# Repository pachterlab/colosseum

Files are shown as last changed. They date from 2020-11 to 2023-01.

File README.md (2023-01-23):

# colosseum: open source fraction collector



<p>A modular, highly customizable, open source fraction collector.</p>

<p align="center">
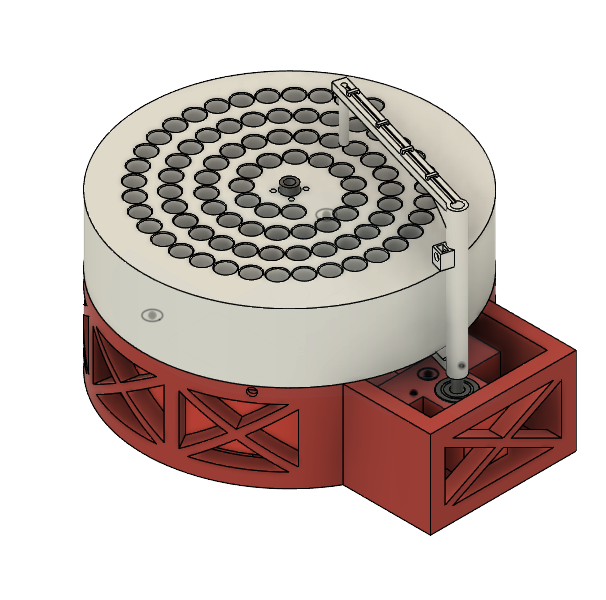
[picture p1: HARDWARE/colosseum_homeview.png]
  
</p>

## Tl;dr
We present colosseum, a low-cost, modular, and automated fluid sampling device for scalable microfluidic applications. The colosseum fraction collector can be built for around $100 using off-the-shelf components, and can be assembled in less than an hour. It uses 3D printed parts and common components that can be easily purchased from many retailers. The device can be run from a Windows, Mac, Linux, or Raspberry Pi computer with an easy-to-use GUI.

<p align="center">
  
</p>

## Table of Contents
1. [What's included?](#whats-included)
2. [Getting Started](#getting-started)
3. [Setting up the hardware](#setting-up-the-hardware)
4. [Installing software](#installing-software)
5. [Startup checklist](#startup-checklist)
6. [Tips/Hints](#tipshints)

## What's included?
* Computer Aided Design (CAD) files of the 3D printed components.
* Controller software (Python) and a graphical user interface (GUI) to control the motor.
* Arduino firmware to send commands to the motors and receive commands from the GUI.
* Bill of materials for sourcing and purchasing materials (up to date as of 1/23/2023).
* Detailed assembly instructions of hardware components.
* Single click executable files for Mac, Windows, Linux, and Raspberry Pi systems.
* A web-based GUI you can run from Chrome without the need to install any Python packages.

## Getting Started
__What do I need to buy?__
The bill of materials with prices and vendor links is available on a [Google Spreadsheet](https://docs.google.com/spreadsheets/d/1GIEj9inR2iLPjJAIjU8kLb73kE2cRr2A/edit?usp=sharing&ouid=103028993012652280196&rtpof=true&sd=true).

__What do I need to make?__
The 3D printed components can be fabricated on any desktop fused filament fabrication (FFF) 3D printer. They were designed using Autodesk Fusion 360, a proprietary CAD software that offers free academic licenses. STL, STEP, IGES, Fusion 360 archive files, and bill of materials are available in the HARDWARE/ folder. They can be used with any slicing software to generate GCode for 3D printing. Here is a [Fusion 360 view](https://a360.co/3r0DND4) of colosseum:

## Setting up the hardware
We have four 3D printed parts for colosseum, which are:
* tube rack
* base
* base plate (support needed)
* dispenser arm (support needed)

The print parameter for these parts are as follows:
* 1.75 mm diameter PLA filament
* nozzle temperature: 215°C
* bed temperature of 60°C
* 10% infill
* 0.2 mm layer height for slicing

### Building colosseum
[This video](https://youtu.be/yG7ECh5GO0o) will guide you through the building process of colosseum.

There is also a [step-by-step guide](https://www.protocols.io/private/C715264790E411EBAAD90A58A9FEAC02) of the assembly.

Here are the steps for building colosseum:
1. 3D print components.
2. Attach set screws to the tube bed.
3. Insert small ball bearings into base.
4. Attach rubber feet on base.
5. Insert rotary shaft into base and fix in place with ball bearing.
6. Screw the stepper motor onto the base (with washers on the hex screws) and attach motor couplings.
7. Screw base plate onto base.
8. Insert ball bearings into the slots on base plate.
9. Insert another rotary shaft into arm and fix with set screw.
10. Insert torsion spring into base plate and arm.
11. Slide the tube bed through the center rotary shaft and align with arm.
12. Tighten all set screws and run!

### Setting up the Arduino
We use the Arduino CNC shield to allow for up to three fraction collectors to be controlled from a computer.

The software is configured to run the stepper motors with 200 steps per revolution at 1/4 microstepping, which translates to 800 steps per rotation. To configure this, it is necessary to add a jumper between the M1 pin of the Arduino CNC shield. More information about microstepping can be found in the product page for the DRV8825 Stepper Motor Driver, which is used by the [CNC shield](http://www.zyltech.com/arduino-cnc-shield-instructions/).

The Arduino should be flashed with the motor_serial_com.ino sketch, available in the firmware/ folder.

Make sure to download and install the [AccelStepper library](https://www.airspayce.com/mikem/arduino/AccelStepper/). To install, unzip the zip file to the libraries sub-folder of your sketchbook.

The fraction collector is driven by an Arduino board that interprets commands sent via USB and sends the signals to control the stepper motor movement. For directions on how to flash an arduino please refer to the official guide: https://www.arduino.cc/en/Guide/HomePage

We recommend that you wrap wires in [cable wraps](https://www.amazon.com/dp/B07FW3GTXB/ref=cm_sw_r_tw_dp_fq83Fb2VRK9QQ?_x_encoding=UTF8&psc=1) and placing your Arduino+CNC shield in a case like [this](https://www.thingiverse.com/thing:3125495).

## Installing software
You can run colosseum on Chrome by going to this link: https://pachterlab.github.io/colosseum/. Running colosseum on the browser platform will not require you to install any software.

To run colosseum locally, you can find the GUI script in the `SOFTWARE/` folder. This GUI is used to interface with a Python script that controls the Arduino via USB.

<p align="center">
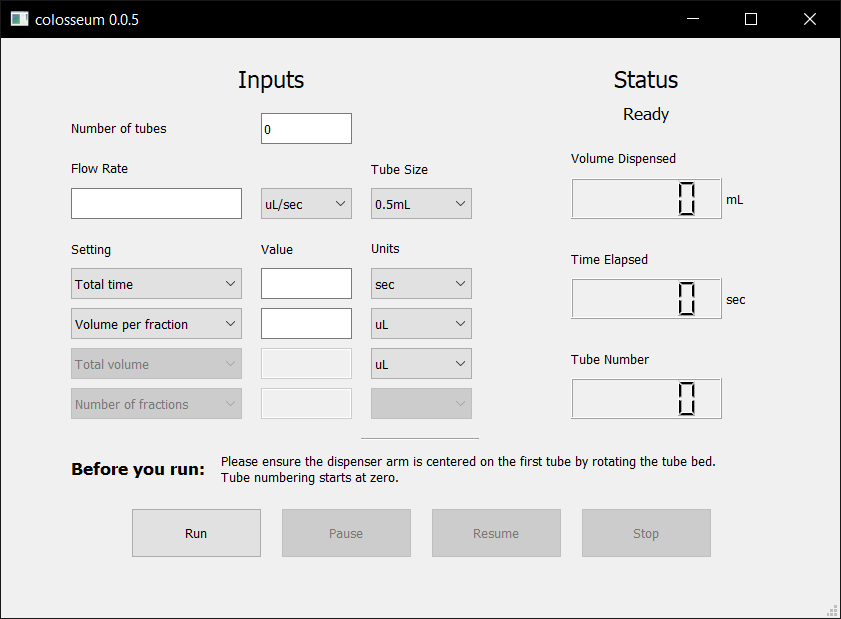
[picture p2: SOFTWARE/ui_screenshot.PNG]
  
</p>

The GUI is provided as a standalone Python package, installable with `pip`. To
install the latest official release, open up the terminal and type:
```
pip install colosseum-ui
```
The Colosseum GUI is now installed and can be started by typing `colosseum` in the termnal. Before you run the system, MAKE SURE YOU HAVE INSTALLED THE ARDUINO FIRMWARE!!

### Manual installation
You may also install the GUI manually by opening up the terminal inside the `SOFTWARE/` folder and typing:
```
pip install .
```

If you get the following error when trying to run `colosseum` on Linux,
```
qt.qpa.plugin: Could not load the Qt platform plugin "xcb" in "" even though it was found.
```
you need to install the appropriate `xcb` library for your Linux distribution.
For Ubuntu users, `xcb` can be installed with the following command:
```
sudo apt install libxcb-xinerama0
```

## Startup Checklist
Before starting the Python controller, make sure
* The Arduino has the firmware uploaded to it
* The Arduino is connected via USB to the computer
* You have appropriately placed jumpers on the CNC Shield to allow for microstepping and hardware enabling (discussed in build video).
* The CNC shield is powered, and that all motors are plugged in to the CNC shield
* The dispenser arm is above the center of the first tube.

## Tips/Hints
Things that we have learned along the way that may help with your build.
* The first tube can be used as a drip tube to catch any drips before you actually start collecting fractions. It will be numbered 0 on the GUI.
* If you hear a scratching noise while you rotate the tube rack, it means that the torsion spring on the arm is scratching the bottom of the tube rack so fold that end of the spring.
* If the dispenser arm does not rotate with the tube rack, it means that the follower on the arm is not correctly touching the grooves of the tube rack.
* Make sure to pull the motor away from the rotary shaft as much as possible so that the pulley belt is taut.

## Safety Considerations
Please review the license before using/developing/distribution colosseum.

The colosseum fraction collector uses 3D printed PLA plastic and standard off the shelf components which do not pose a health hazard if handled correctly. Improper handling of plastics however can create hazards when working with organic solvents.

Before using the colosseum fraction collector in a wetlab environment, please ensure that you have thoroughly tested its functionality for your use case in a dry lab. Once the colosseum fraction collector has been moved into a wetlab, it should not be moved back to a drylab or dry workbench. If you plan to build on the colosseum fraction collector, ensure that you communicate any safety concerns that you may have with your design to potential users and collaborators.

## If you want to contribute to colosseum, feel free to write on the Discussions page on this repo!

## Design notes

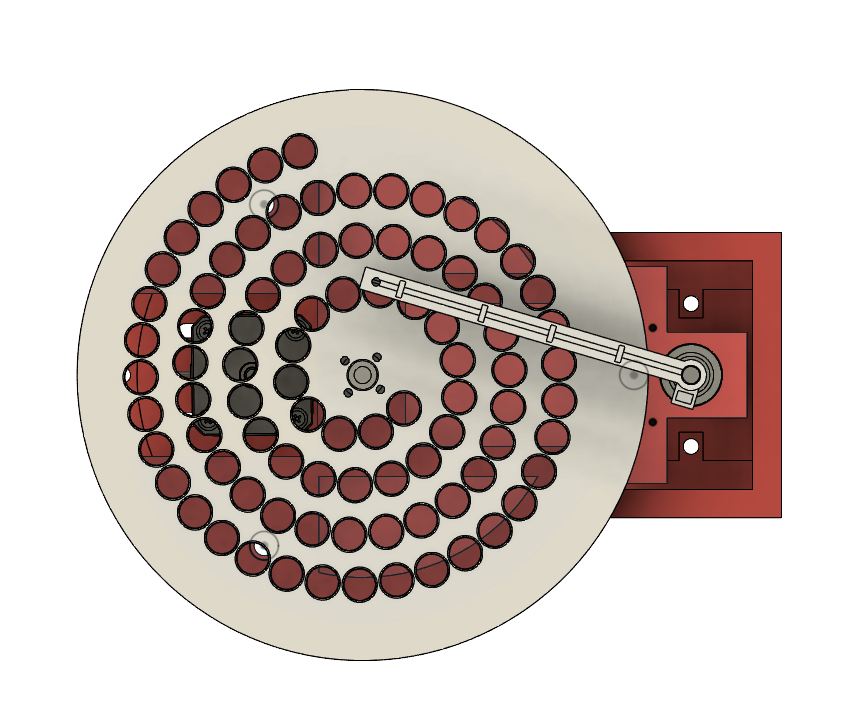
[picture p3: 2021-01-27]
HARDWARE/colosseum_topview.png

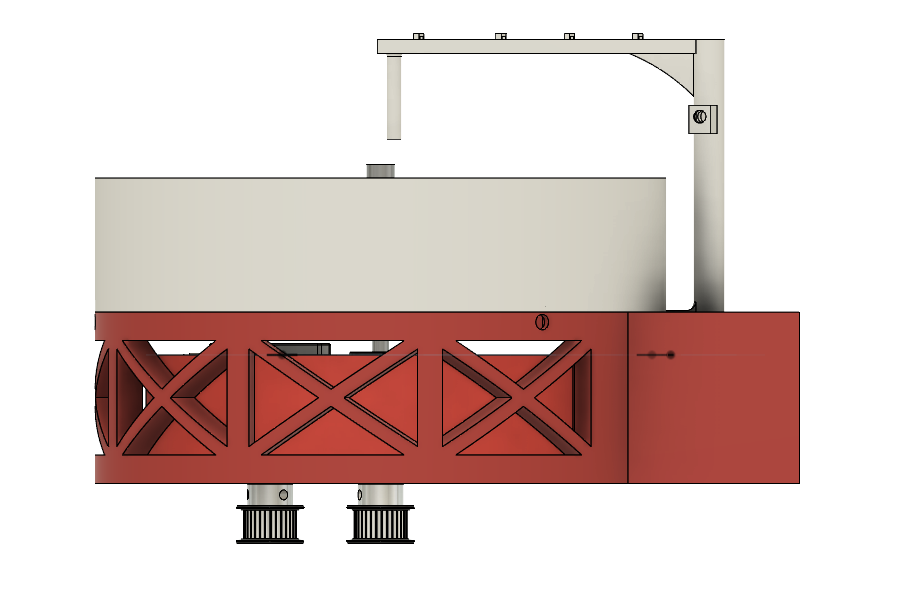
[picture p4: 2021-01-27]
HARDWARE/colosseum_sideview.png

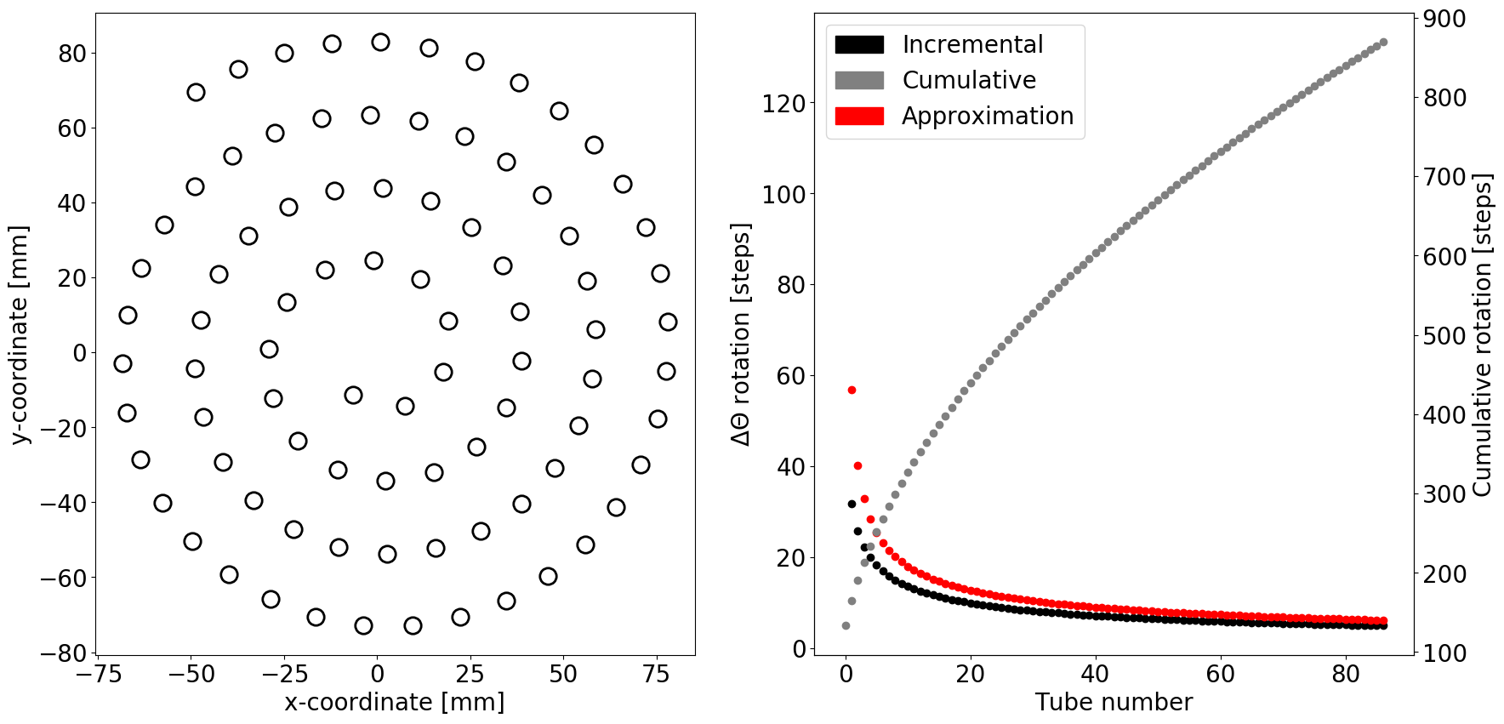
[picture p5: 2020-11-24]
figures/analytical.png

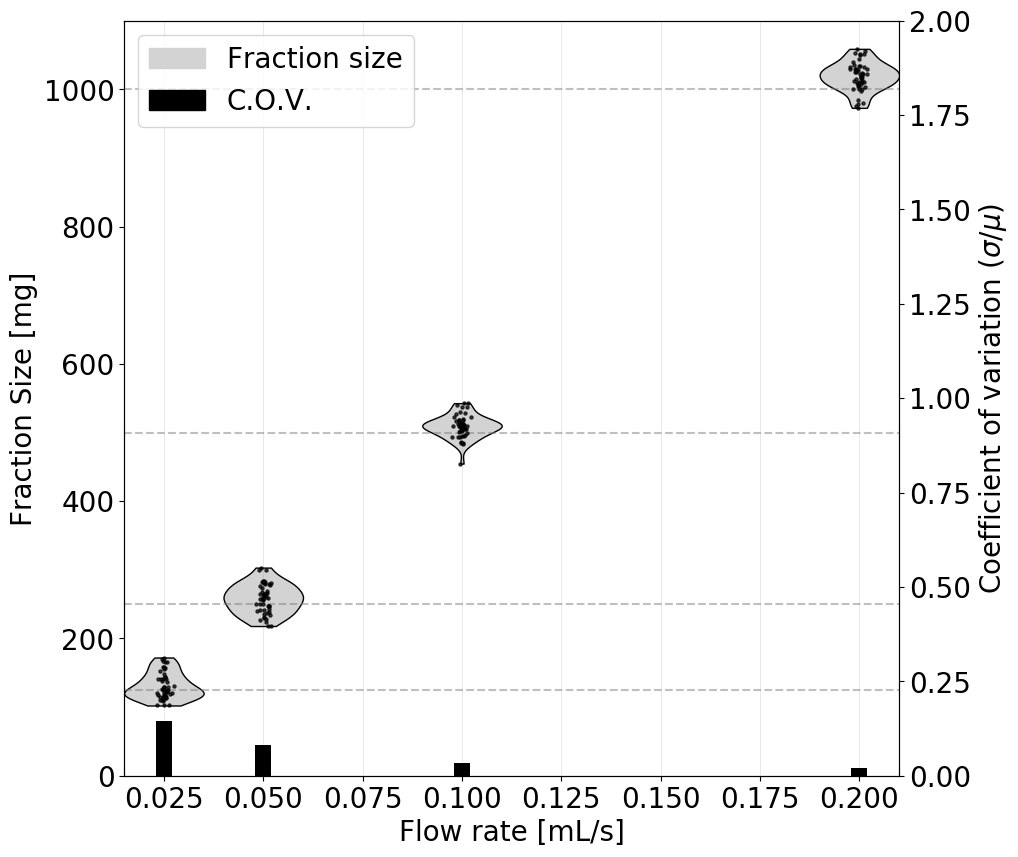
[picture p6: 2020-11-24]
figures/fraction_flowrate.png

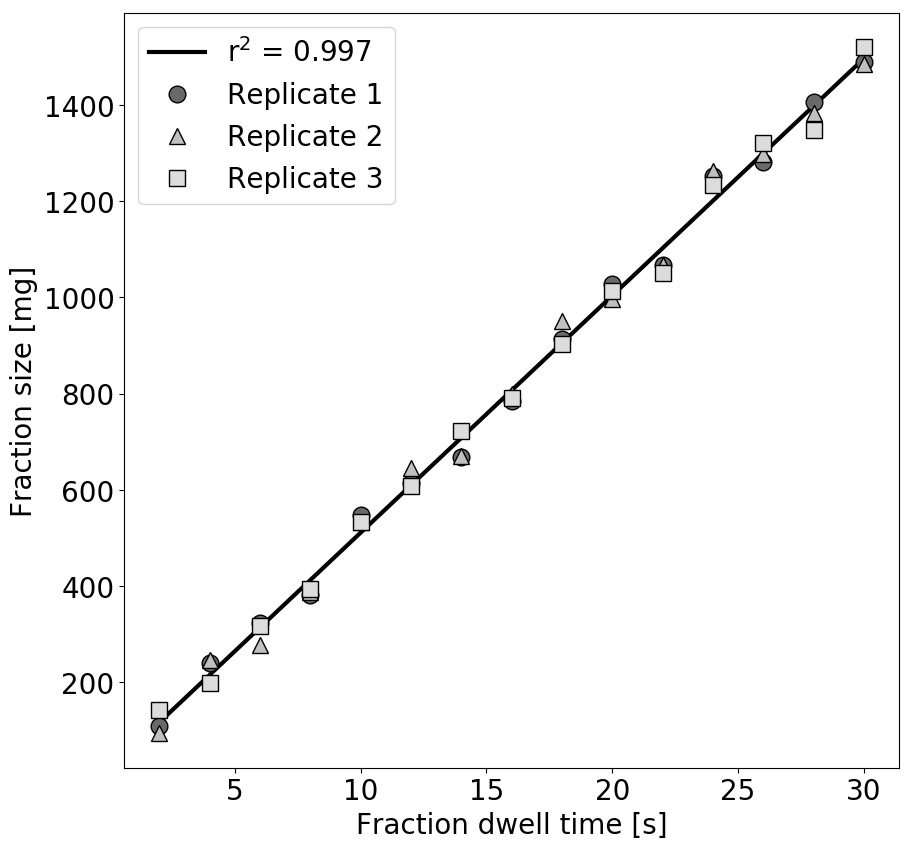
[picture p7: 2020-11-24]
figures/fraction_dwelltime.png

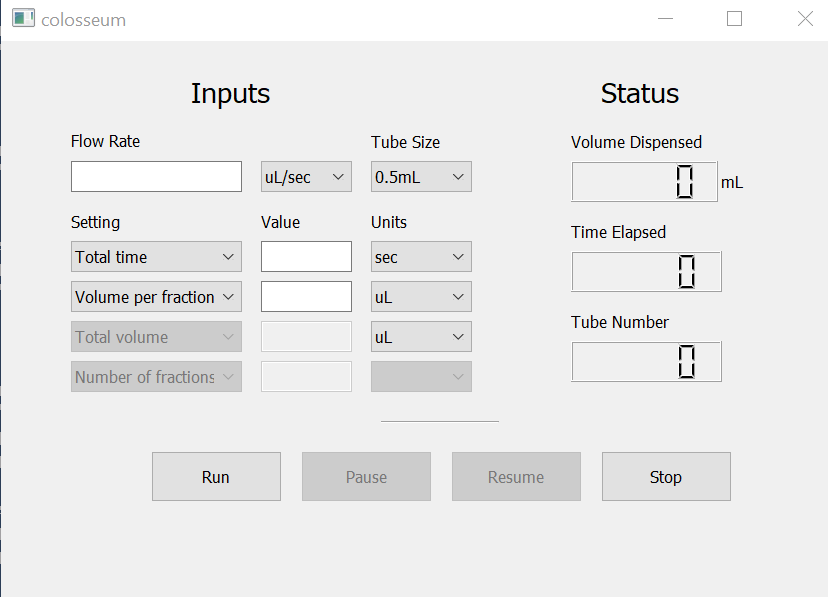
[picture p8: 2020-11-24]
SOFTWARE/colosseum_ui/ui_screenshot.PNG

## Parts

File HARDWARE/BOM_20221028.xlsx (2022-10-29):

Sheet: FracColl
colosseum
Total | $102.29 | *Price may vary based on time of purchase
Part Number | Item Description | Package Cost | Packages for 1 fraction collector | Items per pack | Price per item | Items per fraction collector | Cost for 1 fraction collector | Retailer | Link
1 | 12V power unit (end stripped to fit CNC shield power input) | 15 | 1 | 1 | 15 | 1 | 15 | Amazon | https://www.amazon.com/Kastar-AC-Adapter-Power-LCD/dp/B003TUMDWG?s=electronics
2 | CNC Shield + DRV 8825 Pack | 14.99 | 1 | 1 | 14.99 | 0.25 | 3.7475 | Amazon | https://www.amazon.com/ALMOCN-Printer-Expansion-DRV8825-Stepstick/dp/B09BMVWZGP
3 | Arduino UNO + USB cable | 35.2 | 1 | 1 | 35.2 | 1 | 35.2 | Arduino | https://store-usa.arduino.cc/products/arduino-uno-rev3
4 | Nema 17 Stepper Motor Bipolar 2A 59Ncm 48mm | 13.99 | 1 | 1 | 13.99 | 1 | 13.99 | Amazon | https://www.amazon.com/STEPPERONLINE-Stepper-Bipolar-Connector-compatible/dp/B00PNEQKC0?amp&amp&s=gateway&amp
5 | uxcell HSS Shaft 6mm Dia 150mm Length | 6.96 | 1 | 2 | 3.48 | 2 | 6.96 | Amazon | https://www.amazon.com/uxcell-Lathe-Round-Solid-Length/dp/B07SYHMN6H?s=gateway
6 | uxcell Ball Bearing 6mm x 19mm x 6mm | 6.07 | 1 | 10 | 0.607 | 4 | 2.428 | Amazon | https://www.amazon.com/uxcell-626-2RS-Groove-Bearing-Bearings/dp/B07FMPQP5H?s=gateway
7 | JIUWU 5x10x4mm Miniature Ball Bearing | 7.99 | 1 | 10 | 0.799 | 5 | 3.995 | Amazon | https://www.amazon.com/Miniature-Skateboard-Bearings-MR105ZZ-L-1050ZZ/dp/B00ZHSTKCE?s=gateway
8 | Set Screw Shaft Collar 6mm Bore, 12mm OD, 8mm Width | 21 | 1 | 4 | 5.25 | 2 | 10.5 | Amazon | https://www.amazon.com/Ruland-MSC-6-SS-Collar-Stainless-Metric/dp/B0063KWH7U?s=gateway
9 | WINSINN 2GT Timing Belt Pulley 20 Teeth 5mm Bore 6mm Width | 7.98 | 1 | 5 | 1.596 | 1 | 1.596 | Amazon | https://www.amazon.com/WINSINN-Aluminum-Synchronous-Timing-Printer/dp/B077GNZK3J?s=gateway
10 | WINSINN 2GT Timing Pulley 20 Teeth 6mm Bore 6mm Width | 8.98 | 1 | 5 | 1.796 | 1 | 1.796 | Amazon | https://www.amazon.com/WINSINN-Aluminum-Synchronous-Timing-Printer/dp/B07CXR7SFL?s=gateway
11 | BEMONOC 2GT Rubber Timing Belt 120-2GT-6 60 Teeth | 11.99 | 1 | 10 | 1.199 | 1 | 1.199 | Amazon | https://www.amazon.com/2GT-Timing-Belt-Closed-Loop/dp/B07GQL8ZYH?s=gateway
12 | Hilitchi 110 Pieces Stainless Steel Dowel Pin Assortment Kit | 13.89 | 1 | 110 | 0.1262727273 | 7 | 0.8839090909 | Amazon | https://www.amazon.com/Hilitchi-Stainless-Support-Elements-Assortment/dp/B07F3T5FKL?s=gateway
13 | Round Rubber Feet with Steel Washer Inside | 9.99 | 1 | 10 | 0.999 | 5 | 4.995 | Amazon | https://www.amazon.com/Round-Rubber-Washer-Inside-D19x15xH17mm/dp/B077MB4MGD
 |  | 174.03

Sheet: Sheet1
Fraction Collector
Total | $67.02
Part Number | Item Description | Package Cost | Pkg. for 1 fraction collector | Items per pack | Price per item | Items per fraction collector | Cost for 1 fraction collector | Retailer | Link | Alternative Links (Aliexpress)
1 | 12V power unit (end stripped to fit CNC shield power input) | 15 | 1 | 1 | 15 | 1 | 15 | Amazon | https://amzn.to/2smRmU1
3 | Nema 17 Stepper Motor Bipolar 2A 59Ncm 48mm | 13.99 | 1 | 1 | 13.99 | 1 | 13.99 | Amazon | https://amzn.to/2OsixFJ | https://bit.ly/3poaxEW
4 | uxcell HSS Shaft 6mm Dia 150mm Length | 6.96 | 1 | 2 | 3.48 | 2 | 6.96 | Amazon | https://amzn.to/35GxhXe | https://bit.ly/3rX9U6Z
5 | uxcell Ball Bearing 6mm x 19mm x 6mm | 6.07 | 1 | 10 | 0.607 | 4 | 2.428 | Amazon | https://amzn.to/2q0Z1GZ | https://bit.ly/3b8eYhV
6 | JIUWU 5x10x4mm Miniature Ball Bearing | 7.99 | 1 | 10 | 0.799 | 4 | 3.196 | Amazon | https://amzn.to/2Ovnz49 | https://bit.ly/2ZgT1b8 | (Choose the 5mm x 10mm x 4mm)
7 | Set Screw Shaft Collar 6mm Bore, 12mm OD, 8mm Width | 21 | 1 | 4 | 5.25 | 1 | 5.25 | Amazon | https://amzn.to/2OufigP | https://bit.ly/3u25WM7 | (Choose the 6mm inner diameter model)
8 | WINSINN 2GT Timing Belt Pulley 20 Teeth 5mm Bore 6mm Width | 7.98 | 1 | 5 | 1.596 | 1 | 1.596 | Amazon | https://amzn.to/35K1rsy | https://bit.ly/37euesn | (Choose 5mm bore)
9 | WINSINN 2GT Timing Pulley 20 Teeth 6mm Bore 6mm Width | 8.98 | 1 | 5 | 1.796 | 1 | 1.796 | Amazon | https://amzn.to/2qYr3Dt | https://bit.ly/37euesn | (Choose 6mm bore)
10 | BEMONOC 2GT Rubber Timing Belt 120-2GT-6 60 Teeth | 11.99 | 1 | 10 | 1.199 | 1 | 1.199 | Amazon | https://amzn.to/37IS4Lz | https://bit.ly/3dkWyNJ | (Choose 2GT-120)
11 | Hilitchi 110 Pieces Stainless Steel Dowel Pin Assortment Kit | 13.89 | 1 | 110 | 0.126272727 | 3 | 0.378818182 | Amazon | https://amzn.to/2L285Tl | https://bit.ly/3s0L06f
12 | Round Rubber Feet with Steel Washer Inside | 9.99 | 1 | 10 | 0.999 | 5 | 4.995 | Amazon | https://amzn.to/2XXV1Dq | https://bit.ly/2ZlpYmQ | (Choose 19x15x17)
13 | Torsion Spring 90 Degree Left-Hand Wound, 0.386" OD | 4.63 | 1 | 6 | 0.771666667 | 1 | 0.771666667 | McMaster-Carr | https://www.mcmaster.com/9271k583 | https://bit.ly/3bcJK9B | (Choose 0.8x8x90deg) | Alternative | https://www.amazon.com/dp/B08QN9J157/?coliid=I3IYCJKLM9FWPB&colid=25Z106AEL5JI8 | https://www.amazon.com/dp/B08QNB4M6K/?coliid=I3IYCJKLM9FWPB&colid=25Z106AEL5JI8 | https://www.amazon.com/dp/B08QN8B9CV/?coliid=I3IYCJKLM9FWPB&colid=25Z106AEL5JI8
14 | M3 Hex Screws and Nuts | 10.59 | 1 | 310 | 0.03416129 | 9 | 0.307451613 | Amazon | https://amzn.to/33ABZ7G | https://bit.ly/3poDBfw
15 | M5 Hex Screws and Nuts | 9.99 | 1 | 70 | 0.142714286 | 8 | 1.141714286 | Amazon | https://amzn.to/2OMVYdC
16 | M3 Washers | 8.49 | 1 | 300 | 0.0283 | 4 | 0.1132 | Amazon | https://amzn.to/3rVEjTX | https://bit.ly/3jSpdLi
17 | 6mm Flange Coupling | 11.69 | 1 | 4 | 2.9225 | 1 | 2.9225 | Amazon | https://amzn.to/2YfLFEj | https://bit.ly/3qqrtMr | (Choose 6mm)

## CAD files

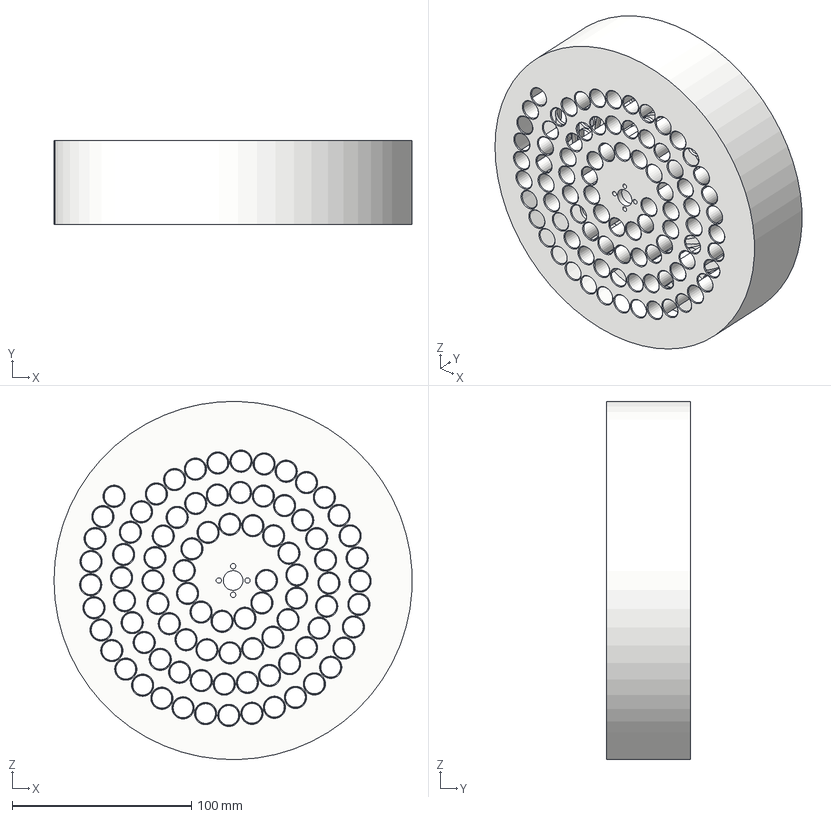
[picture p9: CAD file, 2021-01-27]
HARDWARE/colosseum_tubebed.step
199.9 x 47.0 x 199.9 mm

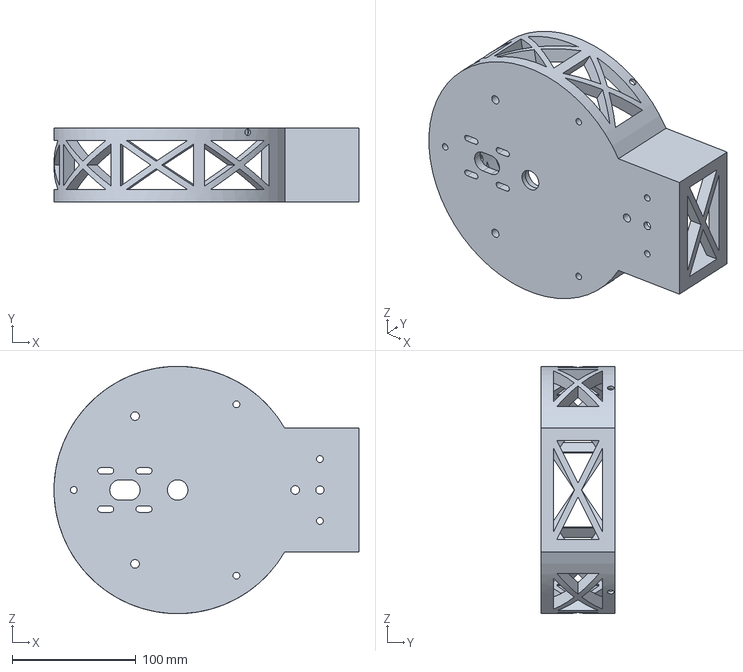
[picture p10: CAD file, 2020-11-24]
HARDWARE/colosseum_base.step
246.6 x 60.0 x 200.0 mm

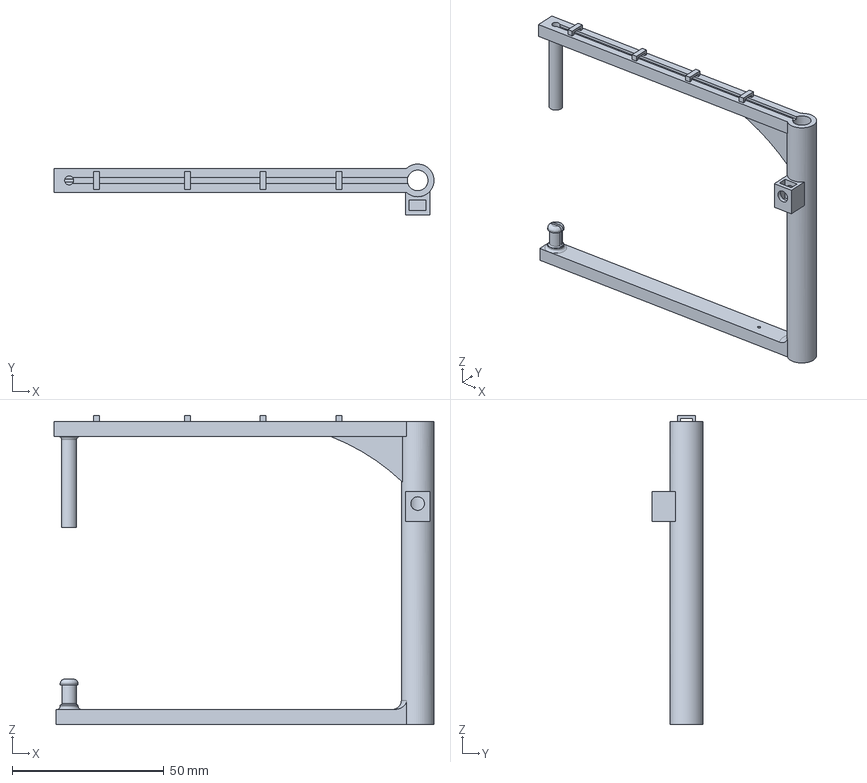
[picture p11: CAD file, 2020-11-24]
HARDWARE/colosseum_arm.step
125.4 x 16.8 x 102.0 mm

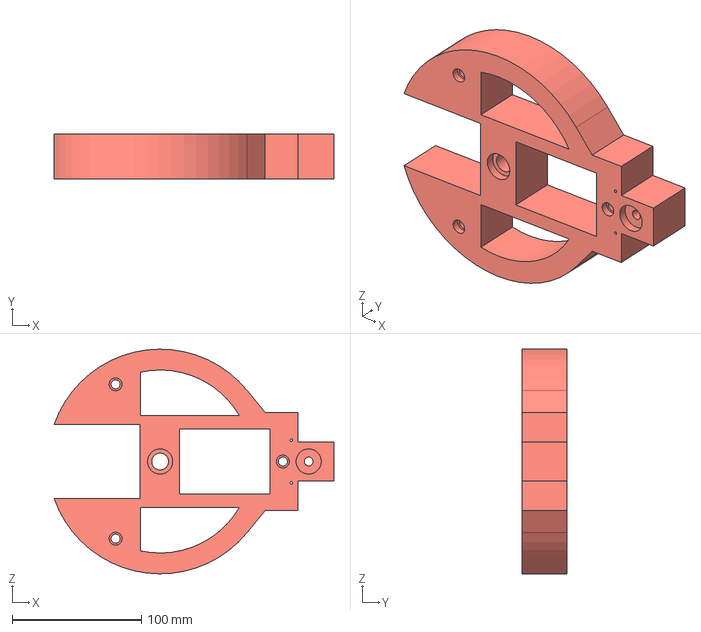
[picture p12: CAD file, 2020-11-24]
HARDWARE/colosseum_baseplate.step
216.8 x 35.0 x 174.0 mm

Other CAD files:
HARDWARE/colosseum_arm.f3d
HARDWARE/colosseum_arm.iges
HARDWARE/colosseum_arm.stl
HARDWARE/colosseum_base.f3d
HARDWARE/colosseum_base.iges
HARDWARE/colosseum_base.stl
HARDWARE/colosseum_baseplate.f3d
HARDWARE/colosseum_baseplate.iges
HARDWARE/colosseum_baseplate.stl
HARDWARE/colosseum_tubebed.f3d
HARDWARE/colosseum_tubebed.iges
HARDWARE/colosseum_tubebed.stl

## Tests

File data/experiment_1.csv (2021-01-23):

Flow rate (uL/s) | Tube Number | Before (g) | After (g) | Difference (g) | Percent error from 1 (%)
6.25 | 1 | 1.066 | 2.063 | 0.997 | -0.3
6.25 | 2 | 1.068 | 2.027 | 0.959 | -4.1
6.25 | 3 | 1.068 | 2.027 | 0.959 | -4.1
6.25 | 4 | 1.068 | 2.079 | 1.011 | 1.1
6.25 | 5 | 1.068 | 2.053 | 0.985 | -1.5
6.25 | 6 | 1.069 | 2.048 | 0.979 | -2.1
6.25 | 7 | 1.045 | 2.04 | 0.995 | -0.5
6.25 | 8 | 1.054 | 2.049 | 0.995 | -0.5
6.25 | 9 | 1.061 | 2.034 | 0.973 | -2.7
6.25 | 10 | 1.063 | 2.078 | 1.015 | 1.5
6.25 | 11 | 1.063 | 2.057 | 0.994 | -0.6
6.25 | 12 | 1.067 | 2.033 | 0.966 | -3.4
6.25 | 13 | 1.062 | 2.067 | 1.005 | 0.5
6.25 | 14 | 1.062 | 2.01 | 0.948 | -5.2
6.25 | 15 | 1.057 | 2.043 | 0.986 | -1.4
6.25 | 16 | 1.06 | 2.026 | 0.966 | -3.4
6.25 | 17 | 1.06 | 2.069 | 1.009 | 0.9
6.25 | 18 | 1.064 | 2.023 | 0.959 | -4.1
6.25 | 19 | 1.065 | 2.061 | 0.996 | -0.4
6.25 | 20 | 1.056 | 2.084 | 1.028 | 2.8
6.25 | 21 | 1.055 | 2.042 | 0.987 | -1.3
6.25 | 22 | 1.072 | 2.029 | 0.957 | -4.3
6.25 | 23 | 1.068 | 2.065 | 0.997 | -0.3
6.25 | 24 | 1.06 | 2.058 | 0.998 | -0.2
6.25 | 25 | 1.064 | 2.064 | 1 | 0
6.25 | 26 | 1.053 | 2.034 | 0.981 | -1.9
6.25 | 27 | 1.054 | 2.063 | 1.009 | 0.9
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

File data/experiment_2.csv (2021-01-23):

Trial | Tube number | Dwell time (s) | Before (g) | After (g) | Difference (g) | Expected (g) | Percent error (%)
1 | 1 | 12 | 1.055 | 1.128 | 0.073 | 0.075 | -2.666666667
1 | 2 | 24 | 1.064 | 1.187 | 0.123 | 0.15 | -18
1 | 3 | 36 | 1.058 | 1.281 | 0.223 | 0.225 | -0.8888888889
1 | 4 | 48 | 1.057 | 1.329 | 0.272 | 0.3 | -9.333333333
1 | 5 | 60 | 1.063 | 1.385 | 0.322 | 0.375 | -14.13333333
1 | 6 | 72 | 1.059 | 1.538 | 0.479 | 0.45 | 6.444444444
1 | 7 | 84 | 1.064 | 1.587 | 0.523 | 0.525 | -0.380952381
1 | 8 | 96 | 1.066 | 1.66 | 0.594 | 0.6 | -1
1 | 9 | 108 | 1.053 | 1.72 | 0.667 | 0.675 | -1.185185185
1 | 10 | 120 | 1.069 | 1.789 | 0.72 | 0.75 | -4
1 | 11 | 132 | 1.066 | 1.895 | 0.829 | 0.825 | 0.4848484848
1 | 12 | 144 | 1.055 | 1.954 | 0.899 | 0.9 | -0.1111111111
1 | 13 | 156 | 1.063 | 2.034 | 0.971 | 0.975 | -0.4102564103
1 | 14 | 168 | 1.063 | 2.042 | 0.979 | 1.05 | -6.761904762
1 | 15 | 180 | 1.063 | 2.257 | 1.194 | 1.125 | 6.133333333
1 | 16 | 192 | 1.054 | 2.239 | 1.185 | 1.2 | -1.25
1 | 17 | 204 | 1.064 | 2.333 | 1.269 | 1.275 | -0.4705882353
1 | 18 | 216 | 1.052 | 2.423 | 1.371 | 1.35 | 1.555555556
1 | 19 | 228 | 1.046 | 2.412 | 1.366 | 1.425 | -4.140350877
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

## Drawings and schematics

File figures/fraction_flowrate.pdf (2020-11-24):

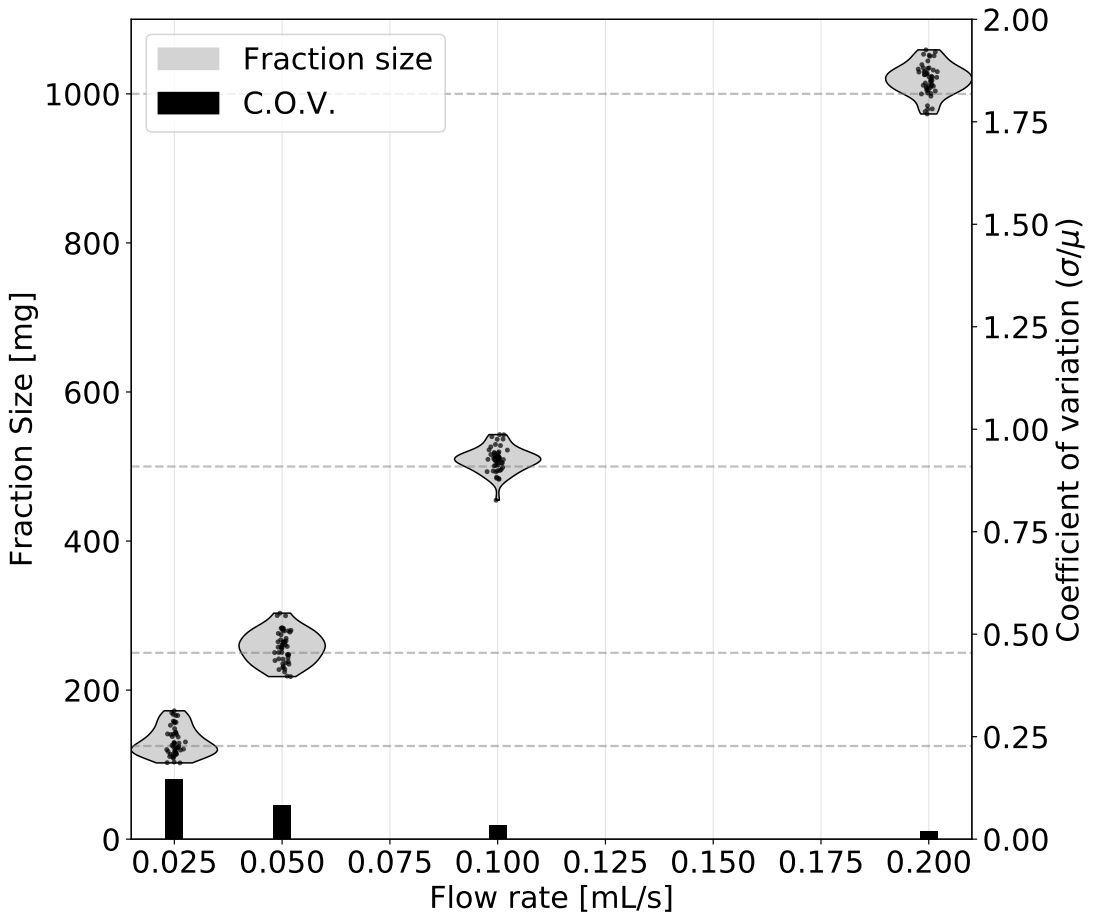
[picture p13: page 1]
ficie; ria; tio; Fraction size C.O.V.

Fraction Size [mg]

Flow rate [mL/s]

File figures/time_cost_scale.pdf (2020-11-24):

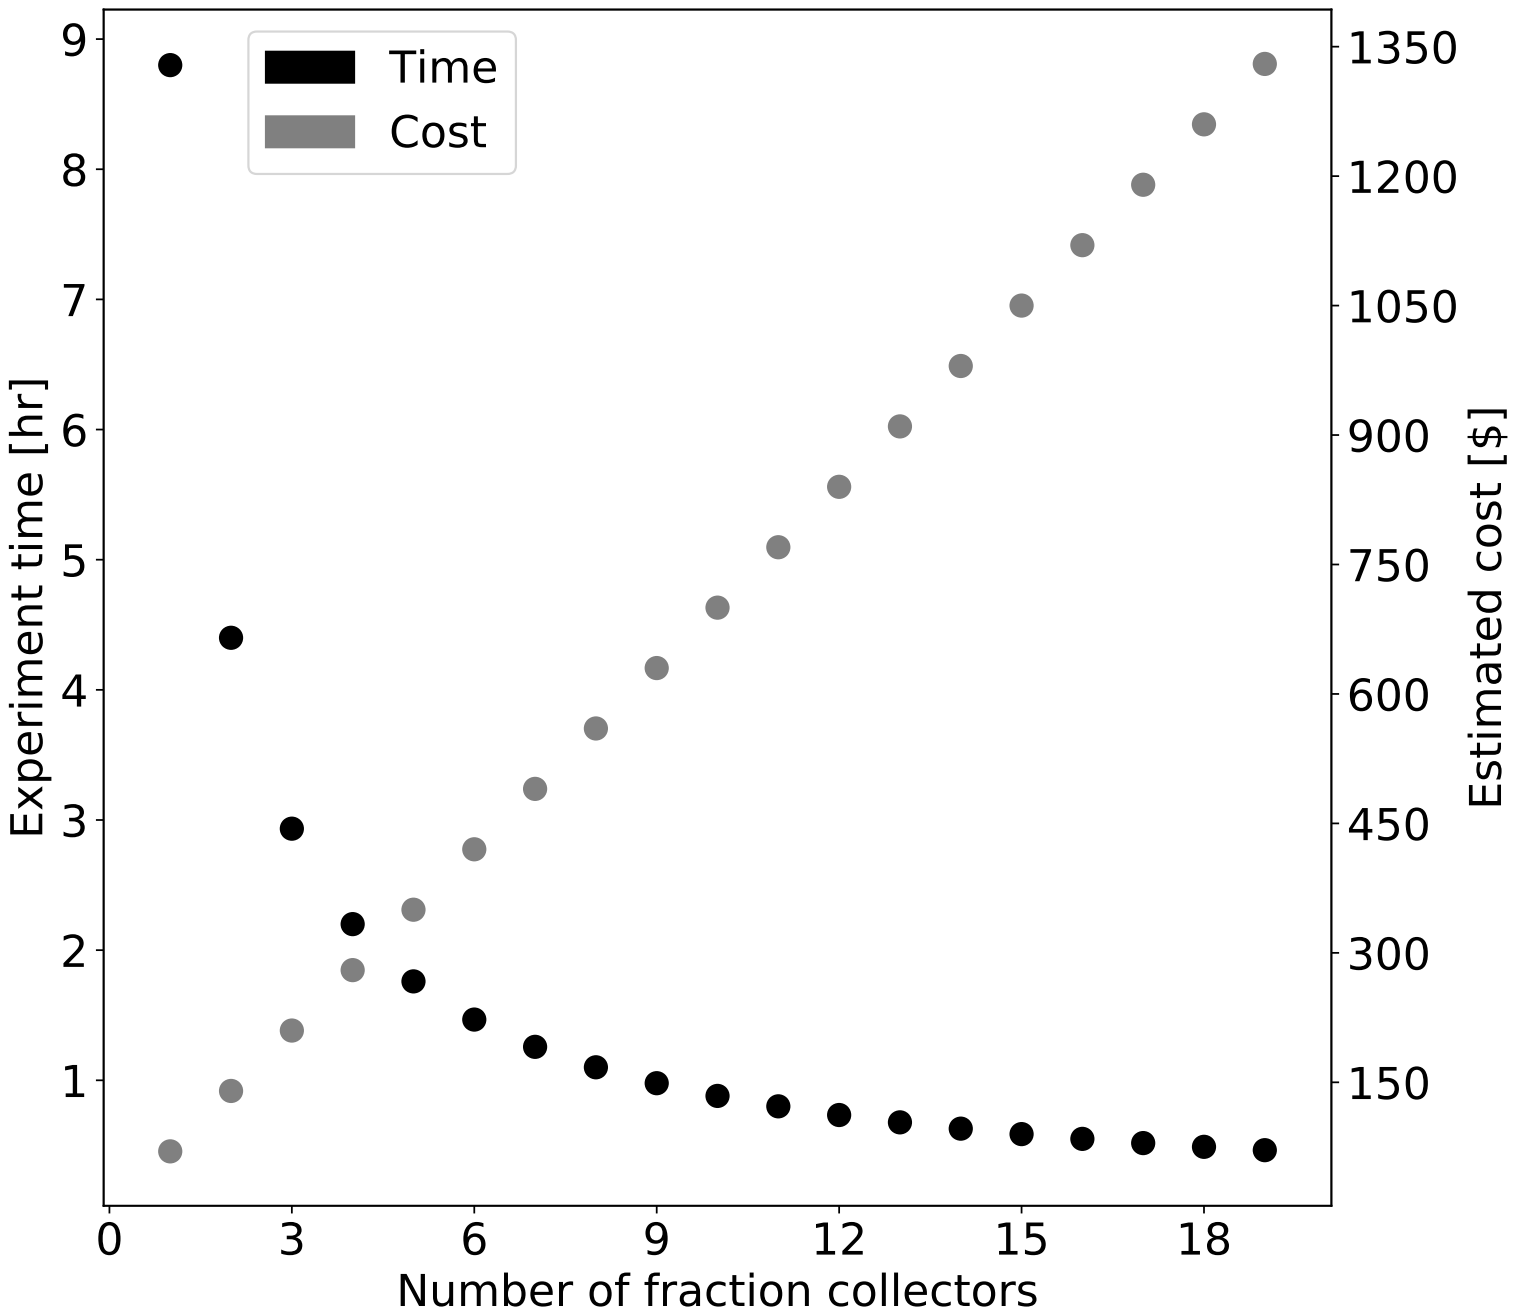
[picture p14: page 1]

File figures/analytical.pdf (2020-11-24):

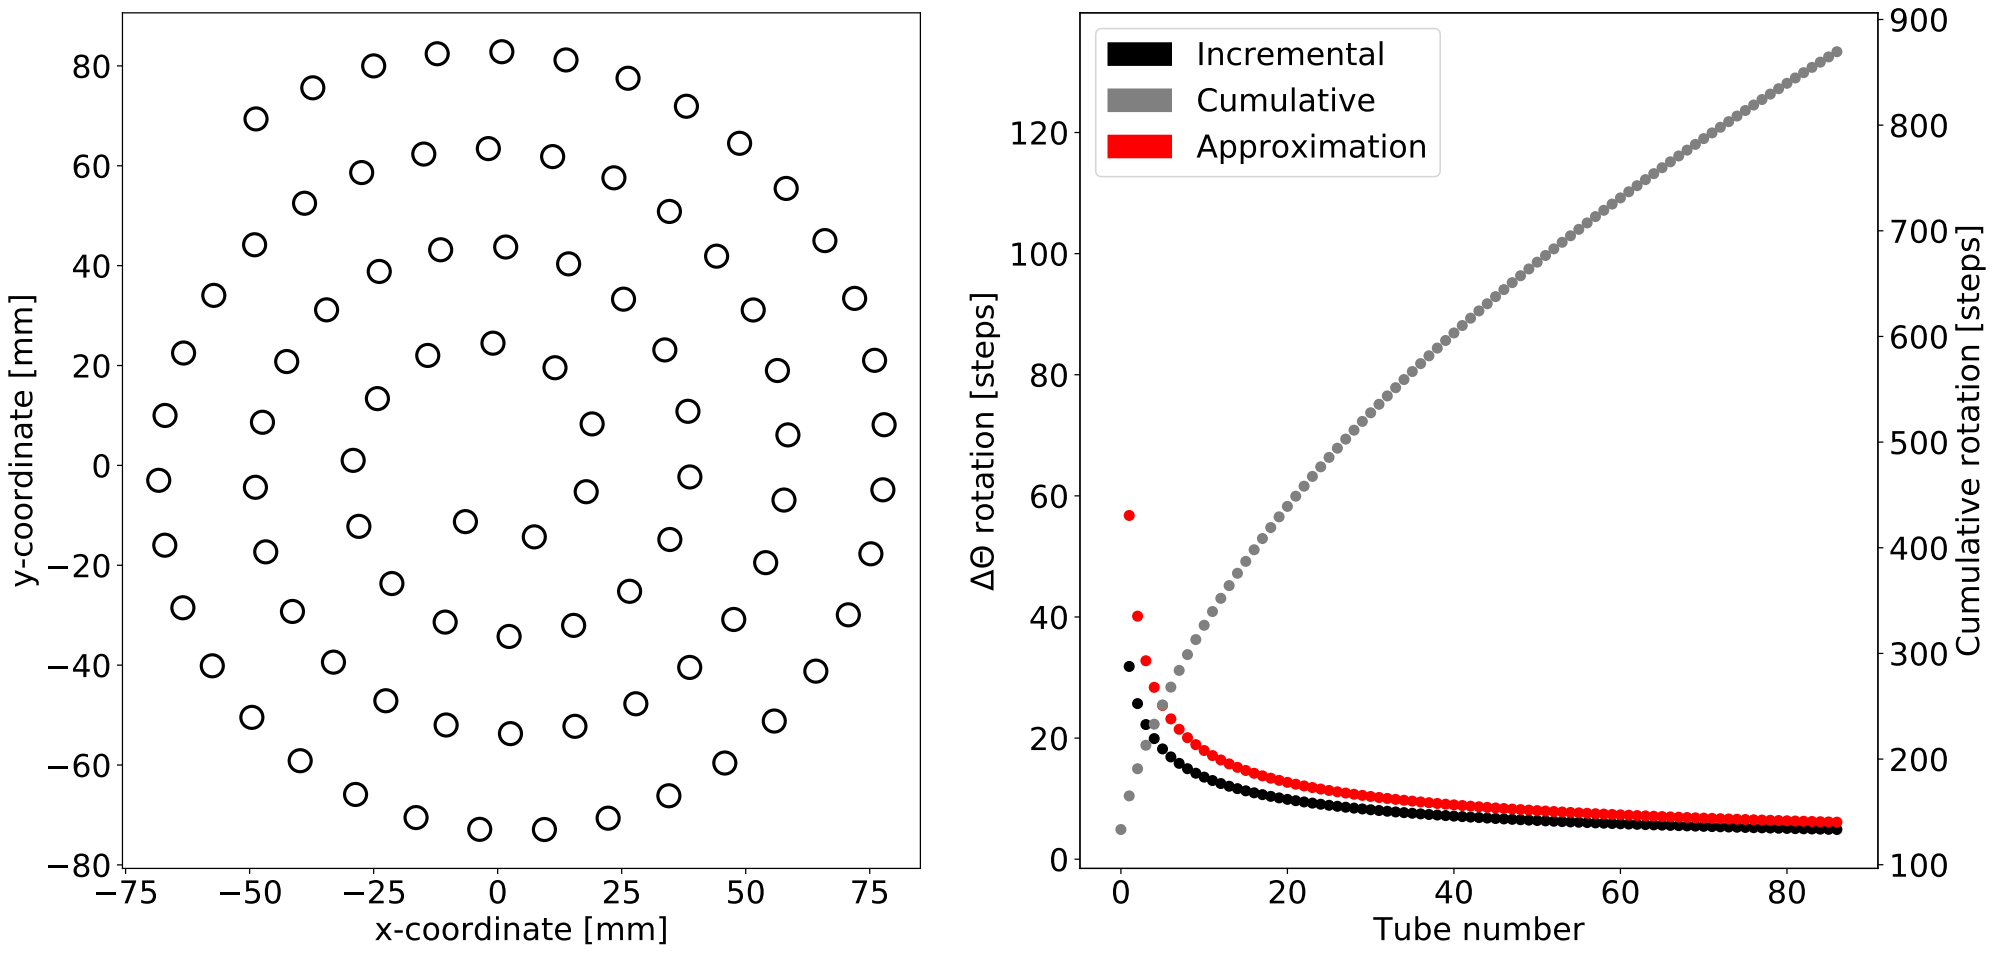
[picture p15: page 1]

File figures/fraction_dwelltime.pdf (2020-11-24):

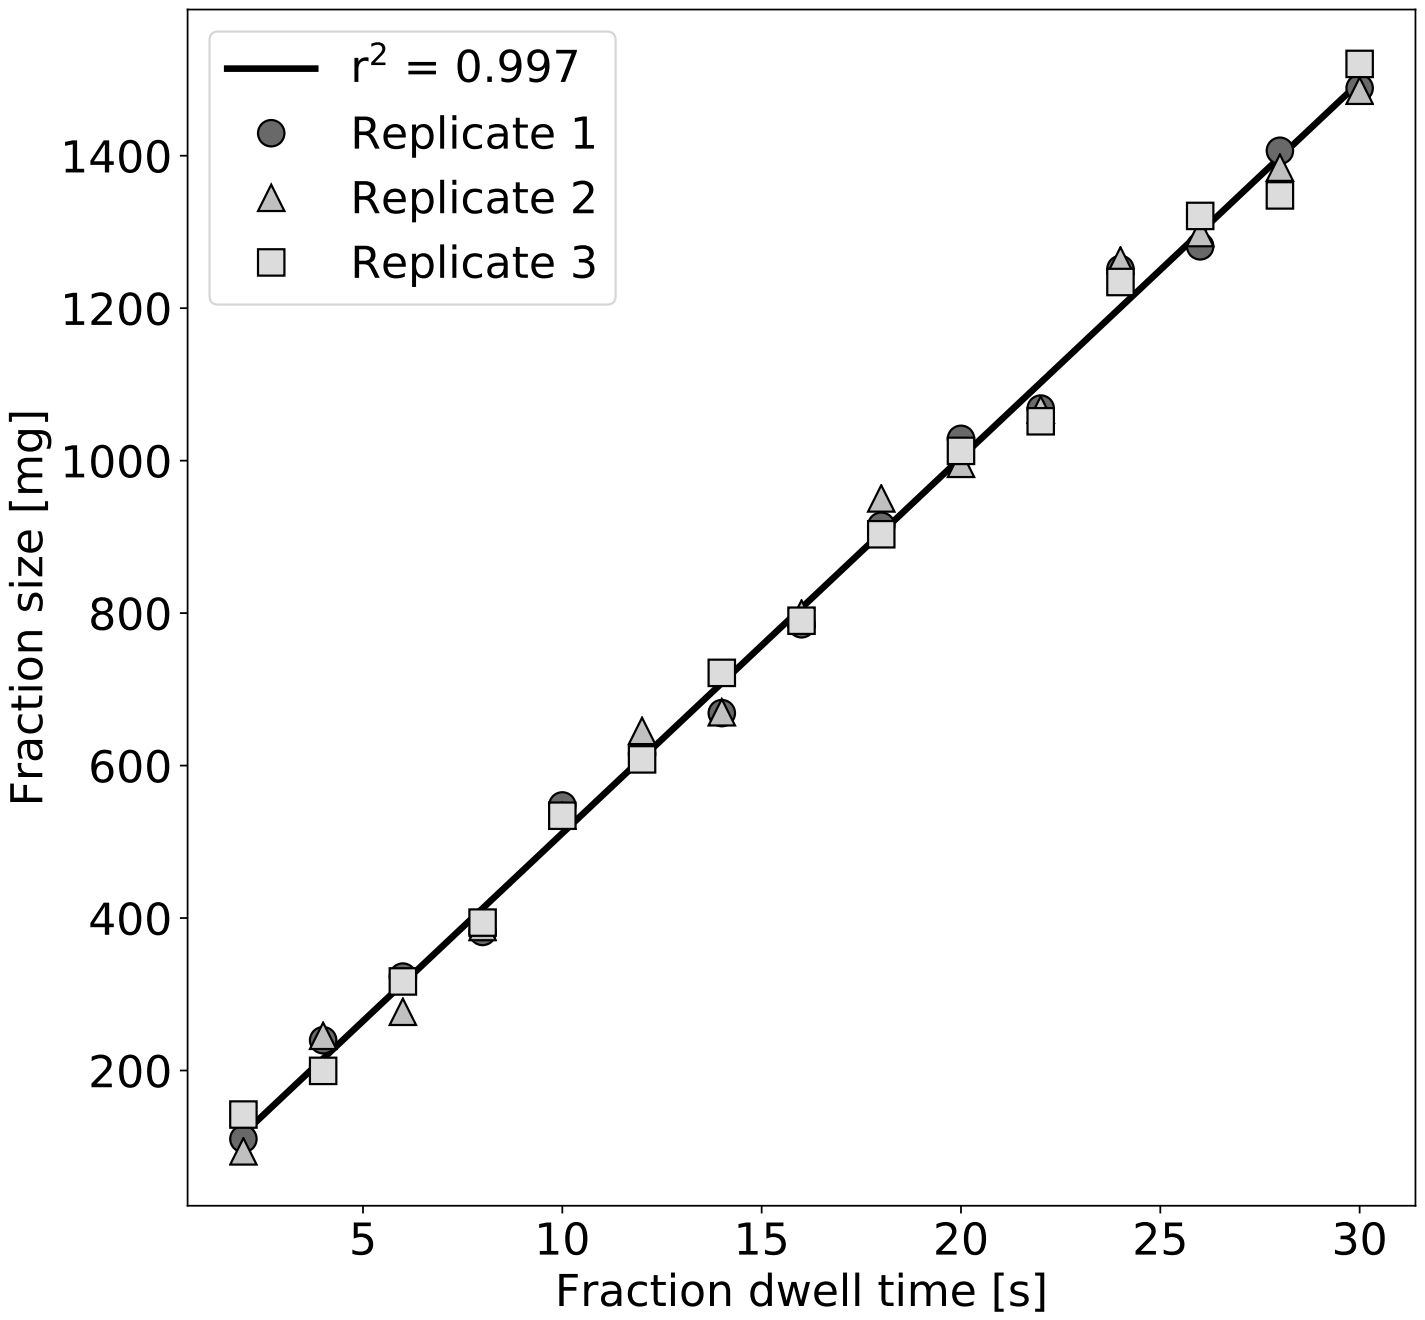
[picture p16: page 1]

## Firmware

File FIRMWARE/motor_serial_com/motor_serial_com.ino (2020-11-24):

#include <AccelStepper.h>
// <RUN,110,1.1,2.4,0.0> test script
// First we create the constants that we will use throughout our code
#define MOTOR_STEPS 200
#define MICROSTEPS 32
#define TOTAL_STEPS 6400

#define X_SPEED 1000 // X steps per second
#define Y_SPEED 1000 // Y
#define Z_SPEED 1000 // Z
float speeds[3] = {X_SPEED, Y_SPEED, Z_SPEED};

#define X_ACCEL 5000.0 // X steps per second per second
#define Y_ACCEL 5000.0 // Y
#define Z_ACCEL 5000.0 // Z
float accels[3] = {X_ACCEL, Y_ACCEL, Z_ACCEL};


#define EN        8       // stepper motor enable, low level effective (note put jumper so automatic)

#define X_DIR     5       // X axis, direction pin
#define Y_DIR     6       // Y
#define Z_DIR     7       // Z

int dir_pins[3] = {X_DIR, Y_DIR, Z_DIR};

#define X_STP     2       // X axis, step pin
#define Y_STP     3       // Y
#define Z_STP     4       // Z

int stp_pins[3] = {X_STP, Y_STP, Z_STP};

#define BAUD_RATE 2000000  // the rate at which data is read

// WRITE COMMAND: <RUN,123,0.0,0.0,0.0>
// <mode, motorID, arg_m1, arg_m2, arg_m3>

// Where mode is ["RUN", "STOP", "RESUME", "PAUSE", "SET_SPEED", "SET_ACCEL"]
// motorID is int [1, 1, 1] (can be combo if numbers ie 100 or 101 or 001 (binary indicator)
// arg_m1 is [any floating number]
// arg_m2 is [any floating number]
// aeg_m3 is [any floating number]


// AccelStepper is the class we use to run all of the motors in a parallel fashion
// Documentation can be found here: http://www.airspayce.com/mikem/arduino/AccelStepper/
AccelStepper stepper1(AccelStepper::DRIVER, X_STP, X_DIR);
AccelStepper stepper2(AccelStepper::DRIVER, Y_STP, Y_DIR);
AccelStepper stepper3(AccelStepper::DRIVER, Z_STP, Z_DIR);
AccelStepper steppers[3] = {stepper1, stepper2, stepper3};

// Now we declare variables we will use throughout our code (That could change!)
const int ledPin = 13;
// The buffer allows us to store bytes as they are read from the python program (64 bytes in size)
const byte buffSize = 64;
char inputBuffer[buffSize];
// We create inputs to this program by <...> where <> represent the startread and endread markers
const char startMarker = '<';
const char endMarker = '>';

byte bytesRecvd = 0;
boolean readInProgress = false;
boolean newDataFromPC = false;
boolean executeCommand = false;

char messageFromPC[buffSize] = {0};
char mode[buffSize] = {0};
int motors[3] = {0, 0, 0};

float value = 0.0;
char dir[buffSize] = {0};
float optional = 0.0;


float arg_m1 = 0.0;
float arg_m2 = 0.0;
float arg_m3 = 0.0;
float args[3] = {arg_m1, arg_m2, arg_m3};

float remainder[3] = {0.0, 0.0, 0.0};

unsigned long curMillis;


typedef void (* FreeFunction )(); // this is a pointer to a function

// Setting up dictionary for easy command execution
typedef struct {
  int mode_idx;
  char* mode;
  FreeFunction function; // now in our FunctionMap type, we can reference a function by its name
} FunctionMap;

int array_sum(int * array, int len) {
  int arraySum;

  arraySum = 0;
  for (int index = 0; index < len; index++)
  {
    arraySum += array[index];
  }
  return arraySum;
}

// All of the functions we would want to run
void _run() {
  for (int i = 0; i < 3; i += 1) {
    if (motors[i] == 1) {
      steppers[i].move(args[i]);
    }
  }

  int stepperStatus[3] = {0, 0, 0};

  // Enable the steppers when in motion
  digitalWrite(EN, LOW);
  while (array_sum(stepperStatus, 3) != array_sum(motors, 3)) {
    // We iterate over the 3 possible steppers
    for (int i = 0; i < 3; i += 1) {
      // If this stepper is selected
      if (motors[i] == 1) {
        // Ask the stepper to move to position at constant speed.
        if (stepperStatus[i] == 0 ) {
          steppers[i].run();
        }
        // Check if it reached it's position
        if (steppers[i].distanceToGo() == 0) {
          // If yes then store that value in the stepperStatus array.
          stepperStatus[i] = 1;
        }
      }
    }
    getDataFromPC();
    if (newDataFromPC) {
      replyToPC(); 
      break;
    }
  }
  // Disable the steppers when not in motion
  digitalWrite(EN, HIGH);
}

void _stop() {
  for (int i = 0; i < 3; i += 1) {
    steppers[i].stop();
  }
}

void _pause() {
  for (int i = 0; i < 3; i += 1) {
    remainder[i] = steppers[i].distanceToGo();
  }

  _stop();
}

void _resume() {
  for (int i = 0; i < 3; i += 1) {
    args[i] = remainder[i];
  }
  _run();
}


void _set_speed() {
  for (int i = 0; i < 3; i += 1) {
    if (motors[i] == 1) {
      steppers[i].setCurrentPosition(0.0);
      steppers[i].setMaxSpeed(args[i]);
      steppers[i].setSpeed(args[i]);
    }
  }
}

void _set_accel() {
  for (int i = 0; i < 3; i += 1) {
    if (motors[i] == 1) {
      steppers[i].setAcceleration(args[i]);
    }
  }
}

const int function_count = 6;
const FunctionMap functions[function_count] {
  {0, "RUN", _run},
  {1, "STOP", _stop},
  {2, "RESUME", _resume},
  {3, "PAUSE", _pause},
  {4, "SET_SPEED", _set_speed},
  {5, "SET_ACCEL", _set_accel}
};


void setup() {
  Serial.begin(BAUD_RATE);

  pinMode(EN, OUTPUT);
  digitalWrite(EN, HIGH);

  // flash LEDs so we know we are alive
  pinMode(ledPin, OUTPUT);
  digitalWrite(ledPin, HIGH);
  delay(500); // delay() is OK in setup as it only happens once
  digitalWrite(ledPin, LOW);
  delay(500);

  // We will initialize all motors once.
  for (int i = 0; i < 3; i += 1) {
    steppers[i].setMaxSpeed(speeds[i]);
    steppers[i].setSpeed(speeds[i]);
    steppers[i].setAcceleration(accels[i]);
    steppers[i].setCurrentPosition(0.0);

  }

  // tell the PC we are ready
  Serial.println("<Arduino is ready>");
}

void loop() {
  // put your main code here, to run repeatedly:
  curMillis = millis();

  getDataFromPC();
  replyToPC();

  execute();


}

//=============
// Here we get data from the serial port, read it one byte at a time, store each subsequent byte in the buffer (list)
// then read it and declare the values to variables in this code
void getDataFromPC() {

  // If there is data from the serial port
  if (Serial.available() > 0) {
    // turn on the LED to indicate we are receiving
    digitalWrite(ledPin, HIGH);
    // read the a single character
    char x = Serial.read();

    // the order of these IF clauses is significant
    if (x == endMarker) {
      readInProgress = false;
      newDataFromPC = true;
      // clear the buffer
      inputBuffer[bytesRecvd] = 0;
      // and parse the data
      return parseData();
    }

    if (readInProgress) {
      // add the character to the buffer
      inputBuffer[bytesRecvd] = x;
      bytesRecvd ++;
      if (bytesRecvd == buffSize) {
        bytesRecvd = buffSize - 1;
      }
    }

    if (x == startMarker) {
      bytesRecvd = 0;
      readInProgress = true;
    }
    digitalWrite(ledPin, LOW);
  }
}

// Here is where we take the string <...> that we have read from the serial port and parse it
void parseData() {

  // split the data into its parts
  // strtok scans the string inputBuffer until it reaches a "," or a ">"
  // Then we declare the variable associated with that part of the inputBuffer
  // each strtok contiues where the previous call left off

  char * strtokIndx; // this is used by strtok() as an index

  strtokIndx = strtok(inputBuffer, ",");     // get the first part - the mode string
  strcpy(mode, strtokIndx);                  // copy it to messageFromPC

  strtokIndx = strtok(NULL, ",");            // get the third part - the motor ID int
  String motorstr(strtokIndx);

  motors[0] = motorstr[0] - '0'; // This is a hack to turn a char '1' into a int 1
  motors[1] = motorstr[1] - '0';
  motors[2] = motorstr[2] - '0';

  strtokIndx = strtok(NULL, ",");
  arg_m1 = atof(strtokIndx);
  strtokIndx = strtok(NULL, ",");
  arg_m2 = atof(strtokIndx);
  strtokIndx = strtok(NULL, ",");
  arg_m3 = atof(strtokIndx);

  args[0] = arg_m1;
  args[1] = arg_m2;
  args[2] = arg_m3;

  newDataFromPC = true;
}

// Here is where we reply to the PC if we find that we have new data from the PC
// This is executed on everyloop if we detect that we have new data from the pc

void replyToPC() {
  if (newDataFromPC) {

    newDataFromPC = false;
    Serial.print("<");
    Serial.print(mode);
    Serial.print(",");
    Serial.print(String(motors[0])); Serial.print(String(motors[1])); Serial.print(String(motors[2]));
    Serial.print(",");
    Serial.print(args[0]);
    Serial.print(",");
    Serial.print(args[1]);
    Serial.print(",");
    Serial.print(args[2]);
    Serial.println(">");

    executeCommand = true;
  }
}

void execute() {
  if (executeCommand) {
    executeCommand = false;
    for (int i = 0; i < function_count; i++) {
      if (strcmp(mode, functions[i].mode) == 0) {
        return (functions[i].function)(); // this just executes one function but it needs to iterate over all of them
      }
    }
    return;
  }
}

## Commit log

2019-11-29 added model files and bom
    [BOM.xlsx, colosseum_arm.f3d, colosseum_arm.iges, colosseum_arm.step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]
2019-12-11 Added serial_comm and fixed ui.py
    added serial_comm to communicate with arduino, still having problems with connecting to port
2020-09-20 Update README.md
    added 3d printing parameters
2020-11-16 updated gui screenshot and added angles.csv
    [angles.csv]
2020-12-18 renamed tube bed notebook
2020-12-28 Update BOM.xlsx
    Added Amazon links to torsion spring
    [BOM.xlsx]
2021-01-23 New experiment data
    [experiment_1.csv, experiment_2.csv]
2021-01-27 added optimal packing updated to restrict to effective diameter of tube bed and the tubes with buffer
2021-01-27 Updated screenshots and CAD files and BOM
    [BOM.xlsx, colosseum_tubebed.f3d, colosseum_tubebed.iges, colosseum_tubebed.step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]
2021-01-27 Create custom_script_linear_dwell_time.py
    This is the script we used to run experiment 2, the fixed flow rate and linearly increasing time experiment.
2022-10-29 Updated BOM and README
    Prices/availabilities of some parts have changed so they were updated on the BOM. README was updated to reflect changes.
    [BOM.xlsx, BOM_20221028.xlsx]
